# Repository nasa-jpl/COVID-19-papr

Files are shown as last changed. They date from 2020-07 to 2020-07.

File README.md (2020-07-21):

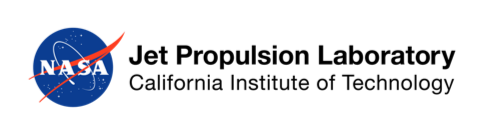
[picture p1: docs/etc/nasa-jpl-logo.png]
Jet Propulsion Laboratory, California Institute of Technology (NASA JPL)
 
# JPL Designed Powered Air-Purifying Respirator (PAPR)

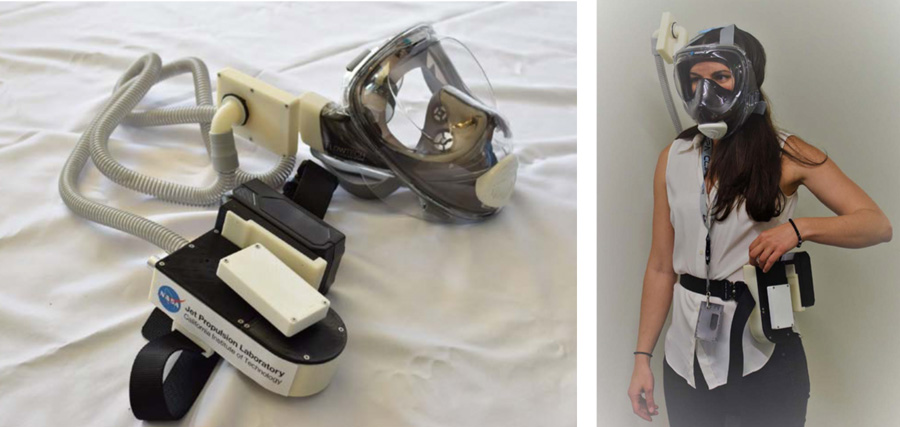
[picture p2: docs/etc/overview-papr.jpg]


In order to help provide Personal Protective Equipment (PPE) for the Coronavirus pandemic, a team at NASA’s Jet Propulsion Laboratory (JPL) has created and tested a 3D printable Powered Air-Purifying Respirator (PAPR) device with custom filters and Commercial Off-The-Shelf (COTS) components. Utilizing a Wildhorn Outfitters® Full Face Snorkel Mask and other COTS equipment, the JPL design is available for use by motivated creators in an Open Source forum readily accessible by anyone wishing to produce the device. Some testing has been performed by JPL and others to verify that it meets the design requirements identified in Public Health Title 42, Code of Federal Regulations, Part 84, but it lacks any NIOSH or other medical institution approval. The device is intended to provide a last line of defense when certified PAPRs are not commercially available.
 
## Getting Started

Read the [full documentation](docs/PAPR_Background_and_Instructions.pdf) to get started. Be sure to reference this document when reviewing the bill of materials and build files listed below.

➡️ [Full Documentation](docs/PAPR_Background_and_Instructions.pdf) 

## Materials Required

The JPL PAPR team has generated a [Bill of Materials (BOM)](docs/Bill_of_Materials.xlsx) for each of the two separate PAPR configurations. The PAPR System top assembly part number is 15180125 with the -1 version signifying the Globe Tools Blower version, and the -2 version signifying the ebmpapst Blower Motor version. These two different versions are functionally the same but slight design changes are included to manage the differences in the blower motor designs. The individual shopping lists are included as separate tabs in the BOM spreadsheet:

➡️ [Bill of Materials (BOM)](docs/Bill_of_Materials.xlsx)

## Build Files

Although the JPL PAPR design uses COTS parts, JPL designed 3D printed parts to package and support these COTS items so the system can perform the intended function. 3D printing enables the home user to download and fabricate these parts independently. The PAPR System top assembly part number is 15180125 with the -1 version signifying the Globe Tools Blower version, and the -2 version signifying the ebmpapst Blower Motor version. These two different versions are functionally the same but slight design changes are included to manage the differences in the blower motor designs.

➡️ [15180125-1 STL Files](15180125-1%20Globe%20Tools%20Blower) (Globe Tools Blower)  
➡️ [15180125-2 STL Files](15180125-2%20ebmPapst%20Blower) (ebmPapst Blower Motor)

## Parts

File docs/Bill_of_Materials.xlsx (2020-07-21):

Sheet: CURRENT BOM
 |  |  |  | PAPR Part and Materials List
 | QTY |  | ITEM NO | PART NO | PART NOMENCLATURE | MATERIAL OR NOTE | MANUFACTURER | Purchasing Link / CAD File Download Source | Minimum Materials Order |  | Price Per PAPR |  | Price Per PAPR |  | Comments
 |  |  |  |  |  |  |  |  |  |  | 105108125 - 1 |  | 105108125 - 2
 | -1 | -2 |  |  |  |  |  |  | Qty | Price, $ | Qty | Price, $ | Qty | Price, $
105108125 Powered Air Purifying Respirator Assembly | 1 | 1 | 1 | Seaview 180 V2 | Snorkel Mask |  | Wildhorn Outfitters | https://www.wildhornoutfitters.com/collections/snorkeling/products/seaview-180-v2-snorkel-mask?variant=10093212041252 | 1 | $74.99 | 1 | $74.99 | 1 | $74.99
 | 1 | 1 | 2 | P09 | Tactical Belt |  | Amazon / Fairwin | https://www.amazon.com/dp/B07V8RMB84/ref=pe_2640190_232748420_TE_item | 2 | $26.99 | 1 | $13.49 | 1 | $13.49 | 2 pack, only need 1. Any belt that can sustain the PAPR weight can be used.
 |  | 1 | 3 | 15180124-2 | Blower Assembly | ABS | JPL Assembly
 | 1 |  | 4 | 15180124-1 | Blower Assembly | ABS | JPL Assembly
 | 2 | 2 | 5 | 15180119-1 | Seal, Round, Filter Adapter | Multipurpose Neoprene Foam Strip | JPL Part |  |  |  |  |  |  |  | Make with 15180118-1, Template, Filter Seal, Round, 3D Printed
 | 1 | 1 | 6 | 15180122-1 | Filter Assembly | ABS | JPL Assembly
 | 1 | 1 | 7 | 15180109-1 | Hose Adapter | ABS | 3D Printed Component | JPL Github
 | 1 | 1 | 8 | 15180112-1 | SeaView 180 V2 Snorkel Mask Side Adapter | ABS | 3D Printed Component | JPL Github
 | QTY |  | ITEM NO | PART NO | PART NOMENCLATURE | MATERIAL OR NOTE | MANUFACTURER | Purchasing Link / CAD File Download Source | Minimum Materials Order |  | Price Per PAPR |  | Price Per PAPR |  | Comments
 |  |  |  |  |  |  |  |  |  |  | 105108125 - 1 |  | 105108125 - 2
 | -1 | -2 |  |  |  |  |  |  | Qty | Price, $ | Qty | Price, $ | Qty | Price, $
15180124 Blower Assembly | 1 | 1 | 9 | 5388k24 | Worm Clamp / Plumbers Tape |  | McMaster-Carr | https://www.mcmaster.com/catalog/5388K24 | 10 | $7.85 | 1 | $0.78 | 1 | $0.78 | OPTIONAL ITEM FOR -1 PAPR DESIGN, NECESSARY FOR -2 PAPR DESIGN 10 pack, need 1
 | 1 | 1 | 10 | SKU: 5797 | Hose, CPAP | Tubing Slim-Style, 48 Inch Length | CPAP SUPPLY USA | https://www.cpapsupplyusa.com/cpapsupplies/tubing/breascpaptubing4ftslim-style.html | 1 | $9.95 | 1 | $9.95 | 1 | $9.95
 | 21 | 23 | 11 | 90065A110 | Screw, C-Sink, Phillips | 18-8 CRES, #4-1/2 in long | McMaster-Carr | https://www.mcmaster.com/catalog/126/3152 | 100 | $3.50 | 21 | $0.73 | 23 | $0.81 | This item is repeated, do not purchase more than what is needed
 | 1 | 1 | 5 | 15180119-1 | Seal, Round, Filter Adapter | Multipurpose Neoprene Foam Strip | JPL Part |  |  |  |  |  |  |  | Make with 15180118-1, Template, Filter Seal, Round, 3D Printed
 | 1 | 1 | 12 | 2935202 | 24V 4ah Battery |  | greenworks | https://www.greenworkstools.com/24v-battery | 1 | $79.99 | 1 | $79.99 | 1 | $79.99 | The 24V, 2AH battery from greenworks will work too but battery life will be significantly reduced
 | 1 |  | 13 | SKU: 702554 | Tubing, 5/8 in ID x 3/4 in OD | Clear Vinyl | Home Depot | https://www.homedepot.com/p/UDP-5-8-in-I-D-x-3-4-in-O-D-x-10-ft-Clear-Vinyl-Tubing-T10006012/304185144 | 10 ft | $9.84 | 1 | $0.16 |  |  | You can replace this component ~ 60 times
 |  | 1 | 14 | 5233K47 | Tubing, 7/8 in ID, 1-1/8 in OD | Clear PVC Plastic | McMaster-Carr | https://www.mcmaster.com/#5233K47 | 10 ft | $14.90 |  |  | 1 | $0.25 | You can replace this component ~ 60 times
 | 1 | 1 | 15 | 15180123-1 | Inlet Filter Assembly |  | JPL Assembly
 | 1 | 1 | 16 | 15180121-1 | Low Flow Alarm System & Electronics Assembly |  | JPL Assembly
 |  | 1 | 17 | 15180101-2 | Housing, ebmpapst Blower |  | 3D Printed Component | JPL Github
 | 1 |  | 18 | 15180101-1 | Housing, Globe Tools Blower |  | 3D Printed Component | JPL Github
 | 1 | 1 | 19 | 15180102-1 | Blower Lid, Universal Blower |  | 3D Printed Component | JPL Github
 | 1 |  | 20 | 15180103-1 | Electronics Lid, Globe Tools Blower |  | 3D Printed Component | JPL Github
 |  | 1 | 21 | 15180103-2 | Electronics Lid, ebmpapst Blower |  | 3D Printed Component | JPL Github
 | 1 | 1 | 22 | 15180104-1 | Battery Holder, Universal Blower |  | 3D Printed Component | JPL Github
 | 2 | 2 | 23 | 15180105-1 | Belt Attachment, Universal Blower |  | 3D Printed Component | JPL Github
 |  | 1 | 24 | 15180107-1 | Blower Mount, ebmpapst Blower |  | 3D Printed Component | JPL Github
 |  | 1 | 25 | 15180108-1 | Controller Mount, ebmpapst Blower |  | 3D Printed Component | JPL Github
 | QTY |  | ITEM NO | PART NO | PART NOMENCLATURE | MATERIAL OR NOTE | MANUFACTURER | Purchasing Link / CAD File Download Source | Minimum Materials Order |  | Price Per PAPR |  | Price Per PAPR |  | Comments
 |  |  |  |  |  |  |  |  |  |  | 105108125 - 1 |  | 105108125 - 2
 | -1 |  |  |  |  |  |  |  | Qty | Price, $ | Qty | Price, $ | Qty | Price, $
15180123 Inlet Filter Assembly | 4 |  | 11 | 90065A110 | Screw, C-Sink, Phillips | 18-8 CRES, #4-1/2 in long | McMaster-Carr | https://www.mcmaster.com/catalog/126/3152 | 100 | $3.50 | 4 | $0.14 | 4 | $0.14 | This item is repeated, do not purchase more than what is needed
 | 1 |  | 26 | 53291 Style Q | HEPA Filter | HEPA Cloth Vacuum Bag | Kenmore | https://www.amazon.com/dp/B07DQ2ZXJV/ (https://www.amazon.com/dp/B07DQ2ZXJV/ref=pe_2640190_232748420_TE_item?th=1) | 2 | $19.99 | 2 | $4.00 | 2 | $4.00 | this is enough material to replace both filters ~ 5 times
 | 1 |  | 27 | 15180113-1 | Inlet Filter Base | ABS | 3D Printed Component | JPL Github
 | 1 |  | 28 | 15180114-1 | Inlet Filter Cover | ABS | 3D Printed Component | JPL Github
 | QTY |  | ITEM NO | PART NO | PART NOMENCLATURE | MATERIAL OR NOTE | MANUFACTURER | Purchasing Link / CAD File Download Source | Minimum Materials Order |  | Price Per PAPR |  | Price Per PAPR |  | Comments
 |  |  |  |  |  |  |  |  |  |  | 105108125 - 1 |  | 105108125 - 2
 | -1 |  |  |  |  |  |  |  | Qty | Price, $ | Qty | Price, $ | Qty | Price, $
15180122 Filter Assembly | 6 |  | 11 | 90065A110 | Screw, C-Sink, Phillips | 18-8 CRES, #4-1/2 in long | McMaster-Carr | https://www.mcmaster.com/catalog/126/3152 | 100 | $3.50 | 6 | $0.21 | 6 | $0.21 | This item is repeated, do not purchase more than what is needed
 | 1 |  | 29 | 93375K404 | Seal, Filter Material | Multipurpose Neoprene Foam Strip | McMaster-Carr | https://www.mcmaster.com/93375K404 | 1 | $14.00 | 1 | $3.50 | 1 | $3.50 | Make with 15180118-2, Template, Filter Seal, 3D Printed. This is enough material to replace seals ~ 4 times
 | 1 |  | 30 | 15180119-2 | Seal, Rectangular, Filter Adapter | Multipurpose Neoprene Foam Strip | JPL Part |  |  |  |  |  |  |  | Make with 15180118-2, Template, Filter Seal, 3D Printed
 | 1 |  | 26 | 53291 Style Q | HEPA Filter | HEPA Cloth Vacuum Bag | Kenmore | https://www.amazon.com/dp/B07DQ2ZXJV/ (https://www.amazon.com/dp/B07DQ2ZXJV/ref=pe_2640190_232748420_TE_item?th=1) | 2 | $19.99 | 2 | $4.00 | 2 | $4.00 | This item is repeated, do not purchase more than what is needed
 | 1 |  | 31 | 15180110-1 | Helmet Filter Base (Sealed 3m) | ABS | 3D Printed Component | JPL Github
 | 1 |  | 32 | 15180111-1 | Helmet Filter Cover (Sealed 3m) | ABS | 3D Printed Component | JPL Github
 | QTY |  | ITEM NO | PART NO | PART NOMENCLATURE | MATERIAL OR NOTE | MANUFACTURER | Purchasing Link / CAD File Download Source | Minimum Materials Order |  | Price Per PAPR |  | Price Per PAPR |  | Comments
 |  |  |  |  |  |  |  |  |  |  | 105108125 - 1 |  | 105108125 - 2
 | -1 |  |  |  |  |  |  |  | Qty | Price, $ | Qty | Price, $ | Qty | Price, $
15180121 Low Flow Sensor & Electronics | 4 |  | 33 | 96817A209 | Screw, Thread-Forming for Thin Plastic, Torx Hd | Zinc Plated Steel, M2 x 6mm long, | McMaster-Carr | https://www.mcmaster.com/catalog/126/3168 | 25 | $6.69 | 4 | $1.07 | 4 | $1.07 | This item is repeated, do not purchase more than what is needed
 | 1 |  | 34 | SFM3300-250-D | Flow Meter |  | Sensirion | https://www.digikey.com/product-detail/en/sensirion-ag/ | 1 | $41.80 | 1 | $41.80 | 1 | $41.80
 | 1 |  | 35 |  | Power Switch (2 state toggle switch) |  | Amazon | https://www.amazon.com/Gadgeter-125VAC-Position-Terminal | 20 | $11.00 | 1 | $0.55 | 1 | $0.55 | 20 pack, need 1
 | 1 |  | 36 | A000005 | Arduino Nano | (Controller for alarm system) | Arduino | https://store.arduino.cc/usa/arduino-nano | 1 | $20.70 | 1 | $20.70 | 1 | $20.70
 | 1 |  | 37 | MP1584EN | Voltage regulator | for Arduino | WGCD | https://www.amazon.com/MP1584EN-DC-DC-Converter-Adjustable-Module/ | 6 | $8.55 | 1 | $1.43 | 1 | $1.43 | Set to 5v and check with multimeter. Alternatively, use 5V set output version made by pololu. 6 pack, need 1
 | 1 |  | 38 | Red LED with Leads | LED | for alarm system | TT Electronics | https://www.digikey.com/product-detail/en/tt-electronics-optek-technology/ | 1 | $0.20 | 1 | $0.20 | 1 | $0.20 | Make sure to use resistor!
 | 1 |  | 39 | 220 Ohm Resistor | Resistor | for LED pull up | Stackpole Electronics | https://www.digikey.com/product-detail/en/stackpole-electronics-inc/ | 1 | $0.10 | 1 | $0.10 | 1 | $0.10 | Used for LED pull up
 | 1 |  | 40 | ECPB_SNAP_BK_3P | Prototype Board |  | ElectroCookie | https://www.amazon.com/gp/product/B08151V9TS/ref=ox_sc_act_title_6?smid=A1S21QI0S59A8I&psc=1 | 12 | $12.00 | 1 | $1.00 | 1 | $1.00 | 12 pack, need 1
 | 1 |  | 41 | a12081600ux0477 | Buzzer |  | Uxcell | https://www.amazon.com/gp/product/B00B0Q4KKO/ref=ox_sc_act_title_5?smid=ATVPDKIKX0DER&psc=1 | 5 | $6.00 | 1 | $1.20 | 1 | $1.20 | 5 pack, need 1
 | 1 |  | 42 |  | 1/8" x 4" Zip Ties |  |  |  |  |  |  |  | 0 | $0.00 | To secure voltage regulator
 | 1 |  | 43 | Jumper wire kit | Jumper wires for various electronics | 24 AWG | Austor | https://www.amazon.com/AUSTOR-Lengths-Assorted-Preformed-Breadboard/ | 1 | $10.99 | 1 | $10.99 | 1 | $10.99 | $10.99 for kit of various lengths. Any 24 AWG or larger wire should work.
 | QTY |  | ITEM NO | PART NO | PART NOMENCLATURE | MATERIAL OR NOTE | MANUFACTURER | Purchasing Link / CAD File Download Source | Minimum Materials Order |  | Price Per PAPR |  | Price Per PAPR |  | Comments
 |  |  |  |  |  |  |  |  |  |  | 105108125 - 1 |  | 105108125 - 2
 | -1 | -2 |  |  |  |  |  |  | Qty | Price, $ | Qty | Price, $ | Qty | Price, $
15180120 Blower Base Electronics | 4 |  | 33 | 96817A209 | Screw, Thread-Forming for Thin Plastic, Torx Hd | Zinc Plated Steel, M2 x 6mm long, | McMaster-Carr | https://www.mcmaster.com/catalog/126/3168 | 25 | $6.69 | 4 | $1.07 |  |  | This item is repeated, do not purchase more than what is needed
 | 1 | 1 | 44 | 8110K1 | Inline Fuse Holder |  | McMaster-Carr | https://www.mcmaster.com/8110K1-8110K1 | 1 | $3.18 | 1 | $3.18 | 1 | $3.18 | Can get these at an auto parts store
 | 1 | 1 | 45 | 7460K521 | Fuse, 2 Amp | ATM mini blade | McMaster-Carr | https://www.mcmaster.com/7460K521 | 5 | $2.61 | 1 | $0.52 | 1 | $0.52 | Can get these at an auto parts store
 | 2 | 2 | 46 | 7060K88 | Single Crimp Male Quick Disconnect Terminal |  | McMaster-Carr | https://www.mcmaster.com/7060K88-7060K88 | 10 | $3.43 | 2 | $0.69 | 2 | $0.69 | 10 pack, need 2
 |  | 1 | 47 | VA-RV45-PAPR | Control Potentiometer |  | ebmpapst | https://www.masterelectronics.com/news/170-free-open-source-respirator-design-from-nasa.aspx | 1 | $0.00 |  |  | 1 | $0.00 | Blower, controller and potentiometer sold in a kit
 |  | 1 | 48 |  | Brushless DC Blower Control Board
 |  | 1 | 49 |  | Brushless DC Blower
 | 1 |  | 50 | WM7040-24V | Control Potentiometer |  | greenworks / Globe Tool |  | 1 | $0.00 | 1 | $0.00 |  |  | Blower, controller and potentiometer sold in a kit
 | 1 |  | 51 |  | Brushless DC Blower Control Board
 | 1 |  | 52 |  | Brushless DC Blower | Manufacturer did continuous operations test 4 hours
 | 1 | 1 | 53 | 16 Gauge Silicone wire | 16 Gauge Silicone wire | 18" of 16 AWG Wire | BNTECHGO | https://smile.amazon.com/BNTECHGO-Silicone-Flexible-Strands-Stranded/dp/B017TFR664 | 1 | $8.48 | 1 | $1.27 | 1 | $1.27 | For use with crimped quick disconnects for battery power. Any 16 AWG or 14 AWG wire should work.
 |  |  |  |  |  |  |  |  | Minimum Materials Order |  | Minimum Supplies Needed
 |  |  |  |  |  |  |  |  | Price, $ |  | Price, $
 |  |  |  | PAPR, 105108125 - 1 |  |  |  |  | $374.98 |  | $276.94
 |  |  |  | PAPR, 105108125 - 2 |  |  |  |  | $387.89 |  | $276.80

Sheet: Shopping List -1 (Globe Tools)
 |  |  | PAPR Part and Materials List
 | QTY | ITEM NO | PART NO | PART NOMENCLATURE | MATERIAL OR NOTE | MANUFACTURER | Purchasing Link / CAD File Download Source | Minimum Materials Order |  | Price Per PAPR |  | Price Per PAPR |  | Comments
 |  |  |  |  |  |  |  |  |  | 105108125 - 1 |  | 105108125 - 2
 |  |  |  |  |  |  |  | Qty | Price, $ | Qty | Price, $ | Qty | Price, $
105108125 Powered Air Purifying Respirator Assembly | 1 | 1 | Seaview 180 V2 | Snorkel Mask | 0 | Wildhorn Outfitters | https://www.wildhornoutfitters.com/collections/snorkeling/products/seaview-180-v2-snorkel-mask?variant=10093212041252 | 1 | $74.99 | 1 | $74.99 | 1 | $74.99 | 0
 | 1 | 2 | P09 | Tactical Belt | 0 | Amazon / Fairwin | https://www.amazon.com/dp/B07V8RMB84/ref=pe_2640190_232748420_TE_item | 2 | $26.99 | 1 | $13.49 | 1 | $13.49 | 2 pack, only need 1. Any belt that can sustain the PAPR weight can be used.
15180124 Blower Assembly | 1 | 9 | 5388k24 | Worm Clamp / Plumbers Tape | 0 | McMaster-Carr | https://www.mcmaster.com/catalog/5388K24 | 10 | $7.85 | 1 | $0.78 | 1 | $0.78 | OPTIONAL ITEM FOR -1 PAPR DESIGN, NECESSARY FOR -2 PAPR DESIGN 10 pack, need 1
 | 1 | 10 | SKU: 5797 | Hose, CPAP | Tubing Slim-Style, 48 Inch Length | CPAP SUPPLY USA | https://www.cpapsupplyusa.com/cpapsupplies/tubing/breascpaptubing4ftslim-style.html | 1 | $9.95 | 1 | $9.95 | 1 | $9.95 | 0
 | 21 | 11 | 90065A110 | Screw, C-Sink, Phillips | 18-8 CRES, #4-1/2 in long | McMaster-Carr | https://www.mcmaster.com/catalog/126/3152 | 100 | $3.50 | 21 | $0.73 | 23 | $0.81 | This item is repeated, do not purchase more than what is needed
 | 1 | 12 | 2935202 | 24V 4ah Battery | 0 | greenworks | https://www.greenworkstools.com/24v-battery | 1 | $79.99 | 1 | $79.99 | 1 | $79.99 | The 24V, 2AH battery from greenworks will work too but battery life will be significantly reduced
 | 1 | 13 | SKU: 702554 | Tubing, 5/8 in ID x 3/4 in OD | Clear Vinyl | Home Depot | https://www.homedepot.com/p/UDP-5-8-in-I-D-x-3-4-in-O-D-x-10-ft-Clear-Vinyl-Tubing-T10006012/304185144 | 10 ft | $9.84 | 1 | $0.16 | 0 |  | You can replace this component ~ 60 times
15180123 Inlet Filter Assembly | 4 | 11 | 90065A110 | Screw, C-Sink, Phillips | 18-8 CRES, #4-1/2 in long | McMaster-Carr | https://www.mcmaster.com/catalog/126/3152 | 100 | $3.50 | 4 | $0.14 | 4 | $0.14 | This item is repeated, do not purchase more than what is needed
 | 1 | 26 | 53291 Style Q | HEPA Filter | HEPA Cloth Vacuum Bag | Kenmore | https://www.amazon.com/dp/B07DQ2ZXJV/ | 2 | $19.99 | 2 | $4.00 | 2 | $4.00 | this is enough material to replace both filters ~ 5 times
15180122 Filter Assembly | 6 | 11 | 90065A110 | Screw, C-Sink, Phillips | 18-8 CRES, #4-1/2 in long | McMaster-Carr | https://www.mcmaster.com/catalog/126/3152 | 100 | $3.50 | 6 | $0.21 | 6 | $0.21 | This item is repeated, do not purchase more than what is needed
 | 1 | 29 | 93375K404 | Seal, Filter Material | Multipurpose Neoprene Foam Strip | McMaster-Carr | https://www.mcmaster.com/93375K404 | 1 | $14.00 | 1 | $3.50 | 1 | $3.50 | Make with 15180118-2, Template, Filter Seal, 3D Printed. This is enough material to replace seals ~ 4 times
 | 1 | 26 | 53291 Style Q | HEPA Filter | HEPA Cloth Vacuum Bag | Kenmore | https://www.amazon.com/dp/B07DQ2ZXJV/ | 2 | $19.99 | 2 | $4.00 | 2 | $4.00 | This item is repeated, do not purchase more than what is needed
15180121 Low Flow Sensor & Electronics | 4 | 33 | 96817A209 | Screw, Thread-Forming for Thin Plastic, Torx Hd | Zinc Plated Steel, M2 x 6mm long, | McMaster-Carr | https://www.mcmaster.com/catalog/126/3168 | 25 | $6.69 | 4 | $1.07 | 4 | $1.07 | This item is repeated, do not purchase more than what is needed
 | 1 | 34 | SFM3300-250-D | Flow Meter | 0 | Sensirion | https://www.digikey.com/product-detail/en/sensirion-ag/ | 1 | $41.80 | 1 | $41.80 | 1 | $41.80 | 0
 | 1 | 35 | 0 | Power Switch (2 state toggle switch) | 0 | Amazon | https://www.amazon.com/Gadgeter-125VAC-Position-Terminal | 20 | $11.00 | 1 | $0.55 | 1 | $0.55 | 20 pack, need 1
 | 1 | 36 | A000005 | Arduino Nano | (Controller for alarm system) | Arduino | https://store.arduino.cc/usa/arduino-nano | 1 | $20.70 | 1 | $20.70 | 1 | $20.70 | 0
 | 1 | 37 | MP1584EN | Voltage regulator | for Arduino | WGCD | https://www.amazon.com/MP1584EN-DC-DC-Converter-Adjustable-Module/ | 6 | $8.55 | 1 | $1.43 | 1 | $1.43 | Set to 5v and check with multimeter. Alternatively, use 5V set output version made by pololu. 6 pack, need 1
 | 1 | 38 | Red LED with Leads | LED | for alarm system | TT Electronics | https://www.digikey.com/product-detail/en/tt-electronics-optek-technology/ | 1 | $0.20 | 1 | $0.20 | 1 | $0.20 | Make sure to use resistor!
 | 1 | 39 | 220 Ohm Resistor | Resistor | for LED pull up | Stackpole Electronics | https://www.digikey.com/product-detail/en/stackpole-electronics-inc/ | 1 | $0.10 | 1 | $0.10 | 1 | $0.10 | Used for LED pull up
 | 1 | 40 | ECPB_SNAP_BK_3P | Prototype Board | 0 | ElectroCookie | https://www.amazon.com/gp/product/B08151V9TS/ref=ox_sc_act_title_6?smid=A1S21QI0S59A8I&psc=1 | 12 | $12.00 | 1 | $1.00 | 1 | $1.00 | 12 pack, need 1
 | 1 | 41 | a12081600ux0477 | Buzzer | 0 | Uxcell | https://www.amazon.com/gp/product/B00B0Q4KKO/ref=ox_sc_act_title_5?smid=ATVPDKIKX0DER&psc=1 | 5 | $6.00 | 1 | $1.20 | 1 | $1.20 | 5 pack, need 1
 | 1 | 42 | 0 | 1/8" x 4" Zip Ties | 0 | 0 | 0 | 0 | $0.00 | 0 | $0.00 | 0 | $0.00 | To secure voltage regulator
 | 1 | 43 | Jumper wire kit | Jumper wires for various electronics | 24 AWG | Austor | https://www.amazon.com/AUSTOR-Lengths-Assorted-Preformed-Breadboard/ | 1 | $10.99 | 1 | $10.99 | 1 | $10.99 | $10.99 for kit of various lengths. Any 24 AWG or larger wire should work.
15180120 Blower Base Electronics | 4 | 33 | 96817A209 | Screw, Thread-Forming for Thin Plastic, Torx Hd | Zinc Plated Steel, M2 x 6mm long, | McMaster-Carr | https://www.mcmaster.com/catalog/126/3168 | 25 | $6.69 | 4 | $1.07 | 0 |  | This item is repeated, do not purchase more than what is needed
 | 1 | 44 | 8110K1 | Inline Fuse Holder | 0 | McMaster-Carr | https://www.mcmaster.com/8110K1-8110K1 | 1 | $3.18 | 1 | $3.18 | 1 | $3.18 | Can get these at an auto parts store
 | 1 | 45 | 7460K521 | Fuse, 2 Amp | ATM mini blade | McMaster-Carr | https://www.mcmaster.com/7460K521 | 5 | $2.61 | 1 | $0.52 | 1 | $0.52 | Can get these at an auto parts store
 | 2 | 46 | 7060K88 | Single Crimp Male Quick Disconnect Terminal | 0 | McMaster-Carr | https://www.mcmaster.com/7060K88-7060K88 | 10 | $3.43 | 2 | $0.69 | 2 | $0.69 | 10 pack, need 2
 | 1 | 50 | WM7040-24V | Control Potentiometer | 0 | greenworks / Globe Tool | 0 | 1 | $0.00 | 1 | $0.00 | 0 |  | Blower, controller and potentiometer sold in a kit
 | 1 | 51 |  | Brushless DC Blower Control Board | 0
 | 1 | 52 |  | Brushless DC Blower | Manufacturer did continuous operations test 4 hours
 | 1 | 53 | 16 Gauge Silicone wire | 16 Gauge Silicone wire | 18" of 16 AWG Wire | BNTECHGO | https://smile.amazon.com/BNTECHGO-Silicone-Flexible-Strands-Stranded/dp/B017TFR664 | 1 | $8.48 | 1 | $1.27 | 1 | $1.27 | For use with crimped quick disconnects for battery power. Any 16 AWG or 14 AWG wire should work.
 |  |  |  |  |  |  |  | Minimum Materials Order |  | Minimum Supplies Needed
 |  |  |  |  |  |  |  | Price, $ |  | Price, $
 |  |  | PAPR, 105108125 - 2 |  |  |  |  | $387.89 |  | $276.80

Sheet: Shopping List -2 (ebmPapst)
 |  |  | PAPR Part and Materials List |  |  |  |  |  |  |  |  |  |  | 0
 |  |  |  |  |  |  |  |  |  |  |  |  |  | 0
 | QTY | ITEM NO | PART NO | PART NOMENCLATURE | MATERIAL OR NOTE | MANUFACTURER | Purchasing Link / CAD File Download Source | Minimum Materials Order |  | Price Per PAPR |  | Price Per PAPR |  | Comments
 |  |  |  |  |  |  |  |  |  | 105108125 - 1 |  | 105108125 - 2
 |  |  |  |  |  |  |  | Qty | Price, $ | Qty | Price, $ | Qty | Price, $
105108125 Powered Air Purifying Respirator Assembly | 1 | 1 | Seaview 180 V2 | Snorkel Mask | 0 | Wildhorn Outfitters | https://www.wildhornoutfitters.com/collections/snorkeling/products/seaview-180-v2-snorkel-mask?variant=10093212041252 | 1 | $74.99 | 1 | $74.99 | 1 | $74.99 | 0
 | 1 | 2 | P09 | Tactical Belt | 0 | Amazon / Fairwin | https://www.amazon.com/dp/B07V8RMB84/ref=pe_2640190_232748420_TE_item | 2 | $26.99 | 1 | $13.49 | 1 | $13.49 | 2 pack, only need 1. Any belt that can sustain the PAPR weight can be used.
15180124 Blower Assembly | 1 | 9 | 5388k24 | Worm Clamp / Plumbers Tape | 0 | McMaster-Carr | https://www.mcmaster.com/catalog/5388K24 | 10 | $7.85 | 1 | $0.78 | 1 | $0.78 | OPTIONAL ITEM FOR -1 PAPR DESIGN, NECESSARY FOR -2 PAPR DESIGN 10 pack, need 1
 | 1 | 10 | SKU: 5797 | Hose, CPAP | Tubing Slim-Style, 48 Inch Length | CPAP SUPPLY USA | https://www.cpapsupplyusa.com/cpapsupplies/tubing/breascpaptubing4ftslim-style.html | 1 | $9.95 | 1 | $9.95 | 1 | $9.95 | 0
 | 23 | 11 | 90065A110 | Screw, C-Sink, Phillips | 18-8 CRES, #4-1/2 in long | McMaster-Carr | https://www.mcmaster.com/catalog/126/3152 | 100 | $3.50 | 21 | $0.73 | 23 | $0.81 | This item is repeated, do not purchase more than what is needed
 | 1 | 12 | 2935202 | 24V 4ah Battery | 0 | greenworks | https://www.greenworkstools.com/24v-battery | 1 | $79.99 | 1 | $79.99 | 1 | $79.99 | The 24V, 2AH battery from greenworks will work too but battery life will be significantly reduced
 | 1 | 14 | 5233K47 | Tubing, 7/8 in ID, 1-1/8 in OD | Clear PVC Plastic | McMaster-Carr | https://www.mcmaster.com/#5233K47 | 10 ft | $14.90 | 0 |  | 1 | $0.25 | You can replace this component ~ 60 times
15180123 Inlet Filter Assembly | 0 | 11 | 90065A110 | Screw, C-Sink, Phillips | 18-8 CRES, #4-1/2 in long | McMaster-Carr | https://www.mcmaster.com/catalog/126/3152 | 100 | $3.50 | 4 | $0.14 | 4 | $0.14 | This item is repeated, do not purchase more than what is needed
 | 0 | 26 | 53291 Style Q | HEPA Filter | HEPA Cloth Vacuum Bag | Kenmore | https://www.amazon.com/dp/B07DQ2ZXJV/ | 2 | $19.99 | 2 | $4.00 | 2 | $4.00 | this is enough material to replace both filters ~ 5 times
15180122 Filter Assembly | 0 | 11 | 90065A110 | Screw, C-Sink, Phillips | 18-8 CRES, #4-1/2 in long | McMaster-Carr | https://www.mcmaster.com/catalog/126/3152 | 100 | $3.50 | 6 | $0.21 | 6 | $0.21 | This item is repeated, do not purchase more than what is needed
 | 0 | 29 | 93375K404 | Seal, Filter Material | Multipurpose Neoprene Foam Strip | McMaster-Carr | https://www.mcmaster.com/93375K404 | 1 | $14.00 | 1 | $3.50 | 1 | $3.50 | Make with 15180118-2, Template, Filter Seal, 3D Printed. This is enough material to replace seals ~ 4 times
 | 0 | 26 | 53291 Style Q | HEPA Filter | HEPA Cloth Vacuum Bag | Kenmore | https://www.amazon.com/dp/B07DQ2ZXJV/ | 2 | $19.99 | 2 | $4.00 | 2 | $4.00 | This item is repeated, do not purchase more than what is needed
15180121 Low Flow Sensor & Electronics | 0 | 33 | 96817A209 | Screw, Thread-Forming for Thin Plastic, Torx Hd | Zinc Plated Steel, M2 x 6mm long, | McMaster-Carr | https://www.mcmaster.com/catalog/126/3168 | 25 | $6.69 | 4 | $1.07 | 4 | $1.07 | This item is repeated, do not purchase more than what is needed
 | 0 | 34 | SFM3300-250-D | Flow Meter | 0 | Sensirion | https://www.digikey.com/product-detail/en/sensirion-ag/ | 1 | $41.80 | 1 | $41.80 | 1 | $41.80 | 0
 | 0 | 35 | 0 | Power Switch (2 state toggle switch) | 0 | Amazon | https://www.amazon.com/Gadgeter-125VAC-Position-Terminal | 20 | $11.00 | 1 | $0.55 | 1 | $0.55 | 20 pack, need 1
 | 0 | 36 | A000005 | Arduino Nano | (Controller for alarm system) | Arduino | https://store.arduino.cc/usa/arduino-nano | 1 | $20.70 | 1 | $20.70 | 1 | $20.70 | 0
 | 0 | 37 | MP1584EN | Voltage regulator | for Arduino | WGCD | https://www.amazon.com/MP1584EN-DC-DC-Converter-Adjustable-Module/ | 6 | $8.55 | 1 | $1.43 | 1 | $1.43 | Set to 5v and check with multimeter. Alternatively, use 5V set output version made by pololu. 6 pack, need 1
 | 0 | 38 | Red LED with Leads | LED | for alarm system | TT Electronics | https://www.digikey.com/product-detail/en/tt-electronics-optek-technology/ | 1 | $0.20 | 1 | $0.20 | 1 | $0.20 | Make sure to use resistor!
 | 0 | 39 | 220 Ohm Resistor | Resistor | for LED pull up | Stackpole Electronics | https://www.digikey.com/product-detail/en/stackpole-electronics-inc/ | 1 | $0.10 | 1 | $0.10 | 1 | $0.10 | Used for LED pull up
 | 0 | 40 | ECPB_SNAP_BK_3P | Prototype Board | 0 | ElectroCookie | https://www.amazon.com/gp/product/B08151V9TS/ref=ox_sc_act_title_6?smid=A1S21QI0S59A8I&psc=1 | 12 | $12.00 | 1 | $1.00 | 1 | $1.00 | 12 pack, need 1
 | 0 | 41 | a12081600ux0477 | Buzzer | 0 | Uxcell | https://www.amazon.com/gp/product/B00B0Q4KKO/ref=ox_sc_act_title_5?smid=ATVPDKIKX0DER&psc=1 | 5 | $6.00 | 1 | $1.20 | 1 | $1.20 | 5 pack, need 1
 | 0 | 42 | 0 | 1/8" x 4" Zip Ties | 0 | 0 | 0 | 0 | $0.00 | 0 | $0.00 | 0 | $0.00 | To secure voltage regulator
 | 0 | 43 | Jumper wire kit | Jumper wires for various electronics | 24 AWG | Austor | https://www.amazon.com/AUSTOR-Lengths-Assorted-Preformed-Breadboard/ | 1 | $10.99 | 1 | $10.99 | 1 | $10.99 | $10.99 for kit of various lengths. Any 24 AWG or larger wire should work.
15180120 Blower Base Electronics | 1 | 44 | 8110K1 | Inline Fuse Holder | 0 | McMaster-Carr | https://www.mcmaster.com/8110K1-8110K1 | 1 | $3.18 | 1 | $3.18 | 1 | $3.18 | Can get these at an auto parts store
 | 1 | 45 | 7460K521 | Fuse, 2 Amp | ATM mini blade | McMaster-Carr | https://www.mcmaster.com/7460K521 | 5 | $2.61 | 1 | $0.52 | 1 | $0.52 | Can get these at an auto parts store
 | 2 | 46 | 7060K88 | Single Crimp Male Quick Disconnect Terminal | 0 | McMaster-Carr | https://www.mcmaster.com/7060K88-7060K88 | 10 | $3.43 | 2 | $0.69 | 2 | $0.69 | 10 pack, need 2
 | 1 | 47 | VA-RV45-PAPR | Control Potentiometer | 0 | ebmpapst | https://www.masterelectronics.com/news/170-free-open-source-respirator-design-from-nasa.aspx | 1 | $0.00 | 0 |  | 1 | $0.00 | Blower, controller and potentiometer sold in a kit
 | 1 | 48 |  | Brushless DC Blower Control Board | 0
 | 1 | 49 |  | Brushless DC Blower | 0
 | 1 | 53 | 16 Gauge Silicone wire | 16 Gauge Silicone wire | 18" of 16 AWG Wire | BNTECHGO | https://smile.amazon.com/BNTECHGO-Silicone-Flexible-Strands-Stranded/dp/B017TFR664 | 1 | $8.48 | 1 | $1.27 | 1 | $1.27 | For use with crimped quick disconnects for battery power. Any 16 AWG or 14 AWG wire should work.
 |  |  |  |  |  |  |  | Minimum Materials Order |  | Minimum Supplies Needed
 |  |  |  |  |  |  |  | Price, $ |  | Price, $
 |  |  | PAPR, 105108125 - 2 |  |  |  |  | $387.89 |  | $276.80

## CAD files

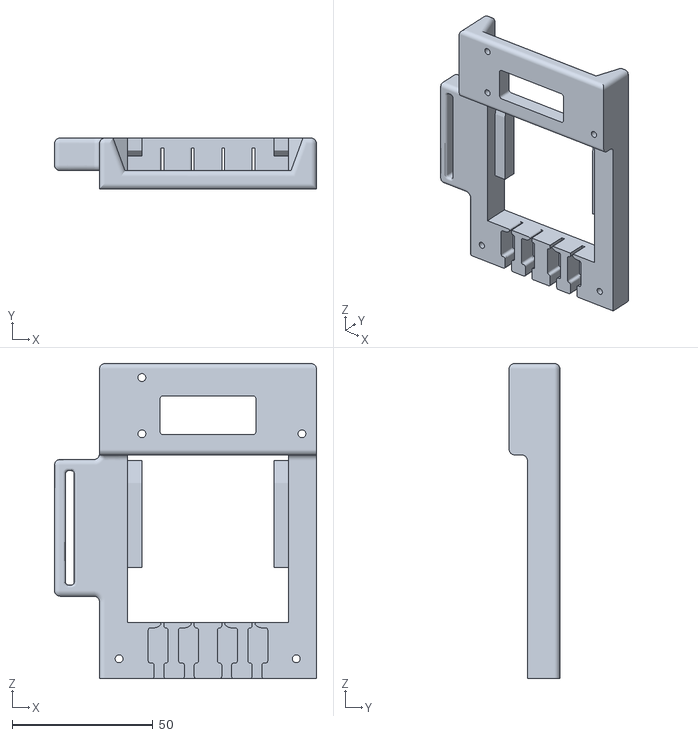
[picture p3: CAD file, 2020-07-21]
15180125-1 Globe Tools Blower/15180104-1_STL.STL
93.2 x 18.1 x 112.0

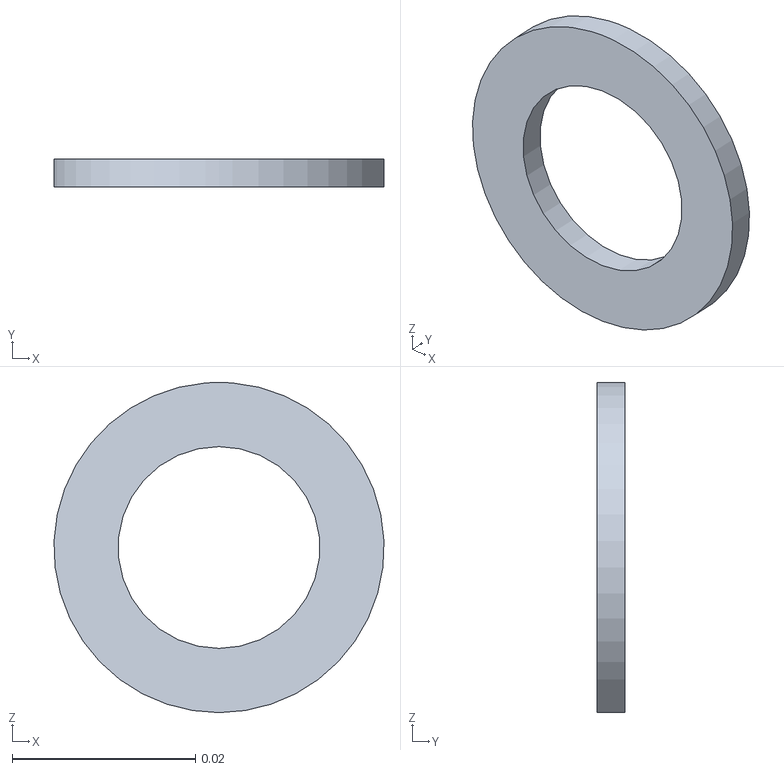
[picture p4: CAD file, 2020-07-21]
15180125-2 ebmPapst Blower/15180118-1_STL.STL
0.036 x 0.003 x 0.036

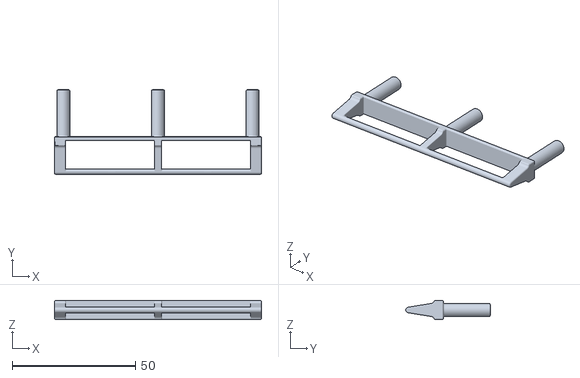
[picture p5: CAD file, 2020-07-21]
15180125-1 Globe Tools Blower/15180116-1_STL.STL
84.0 x 34.3 x 7.75

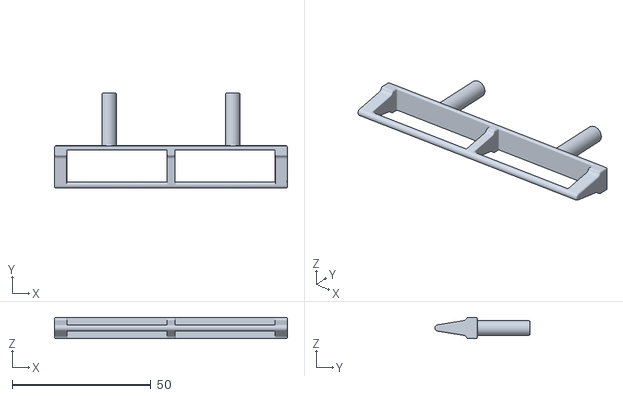
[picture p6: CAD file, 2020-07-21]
15180125-2 ebmPapst Blower/15180117-1_STL.STL
84.0 x 34.3 x 7.75

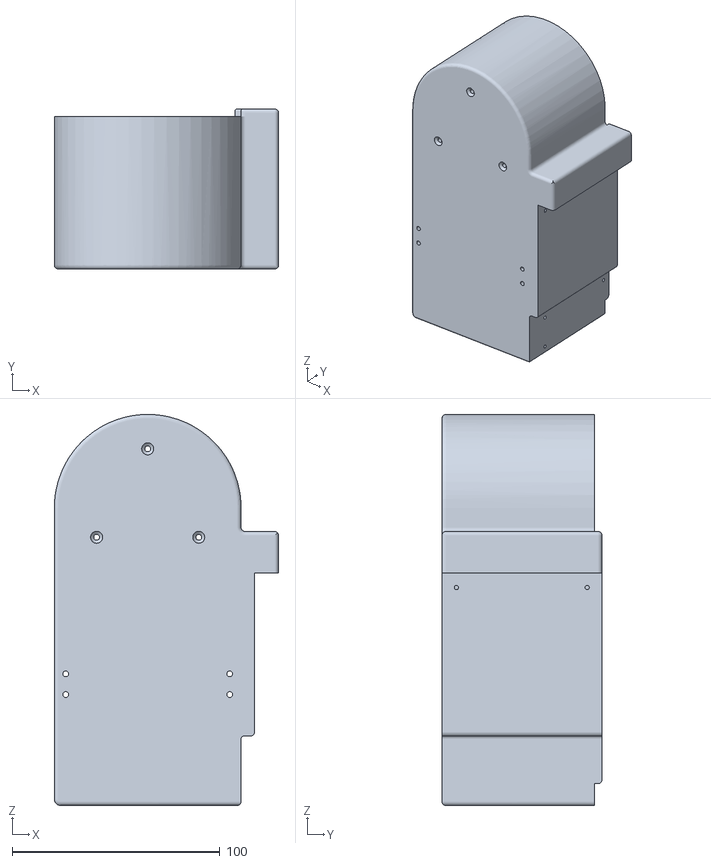
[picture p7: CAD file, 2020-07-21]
15180125-1 Globe Tools Blower/15180101-1_STL.STL
108.1 x 77.2 x 188.4

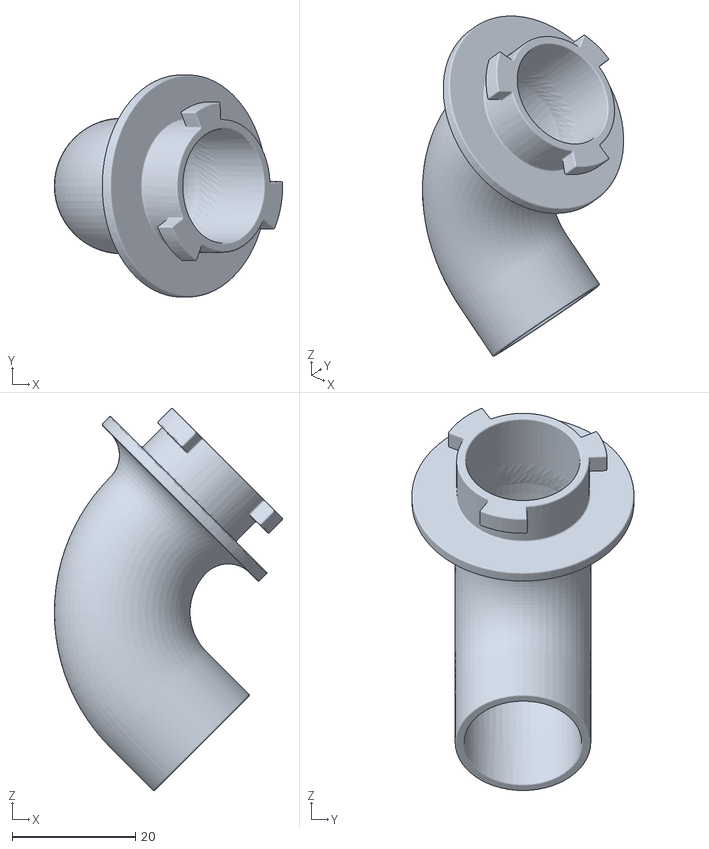
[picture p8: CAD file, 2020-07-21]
15180125-2 ebmPapst Blower/15180109-1_STL.STL
37.0 x 36.0 x 61.9

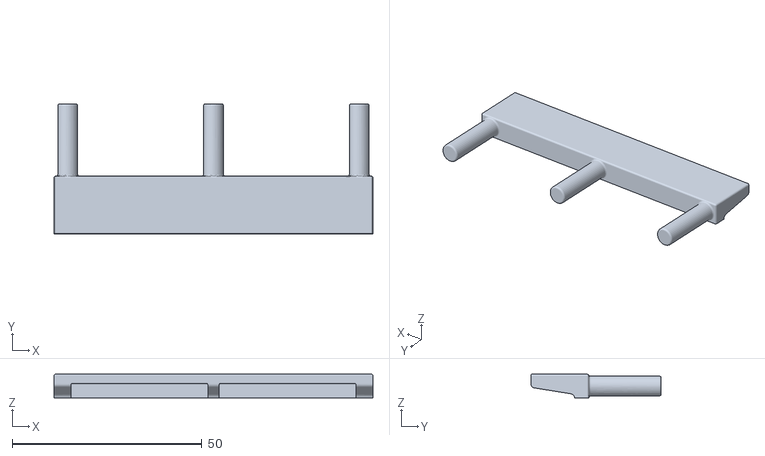
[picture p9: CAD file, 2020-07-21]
15180125-1 Globe Tools Blower/15180115-1_STL.STL
84.0 x 34.3 x 6.25

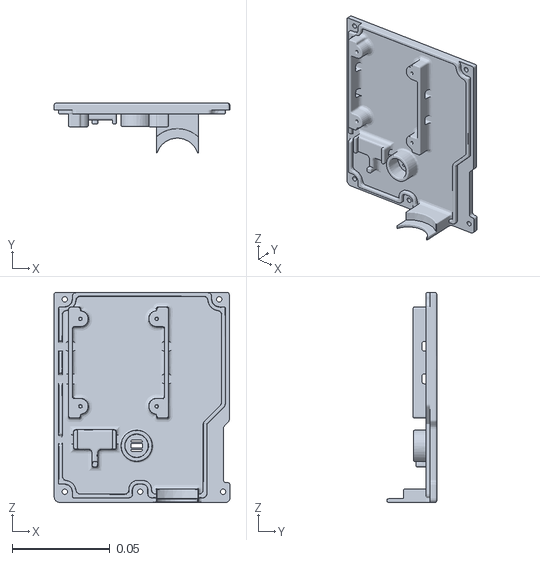
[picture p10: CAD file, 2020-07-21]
15180125-2 ebmPapst Blower/15180103-2_STL.STL
0.09 x 0.0254 x 0.107

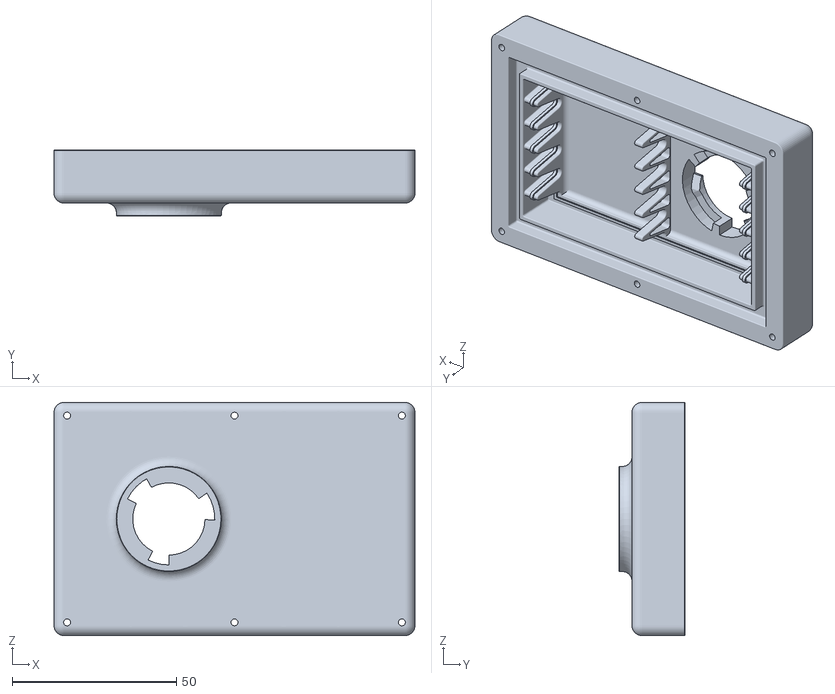
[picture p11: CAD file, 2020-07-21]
15180125-1 Globe Tools Blower/15180110-1_STL.STL
110.0 x 20.2 x 71.0

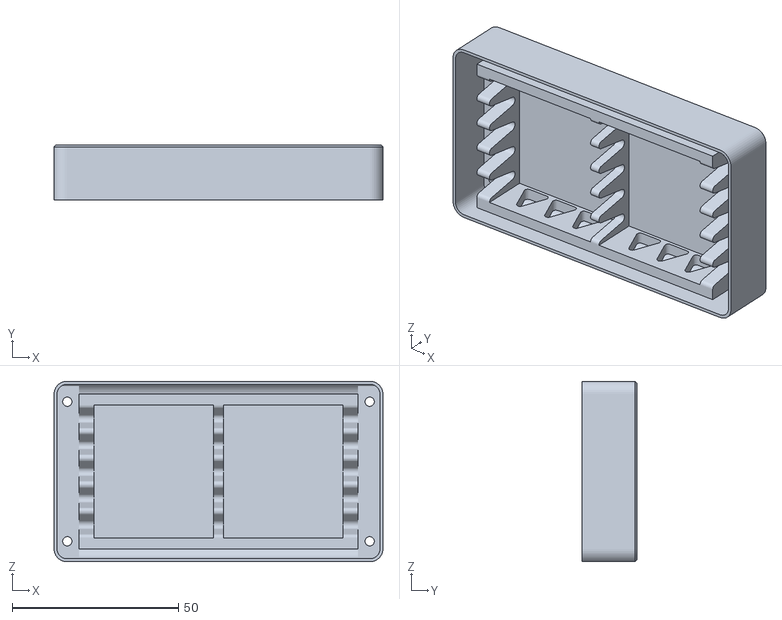
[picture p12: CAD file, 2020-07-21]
15180125-2 ebmPapst Blower/15180114-1_STL.STL
99.0 x 16.6 x 54.3

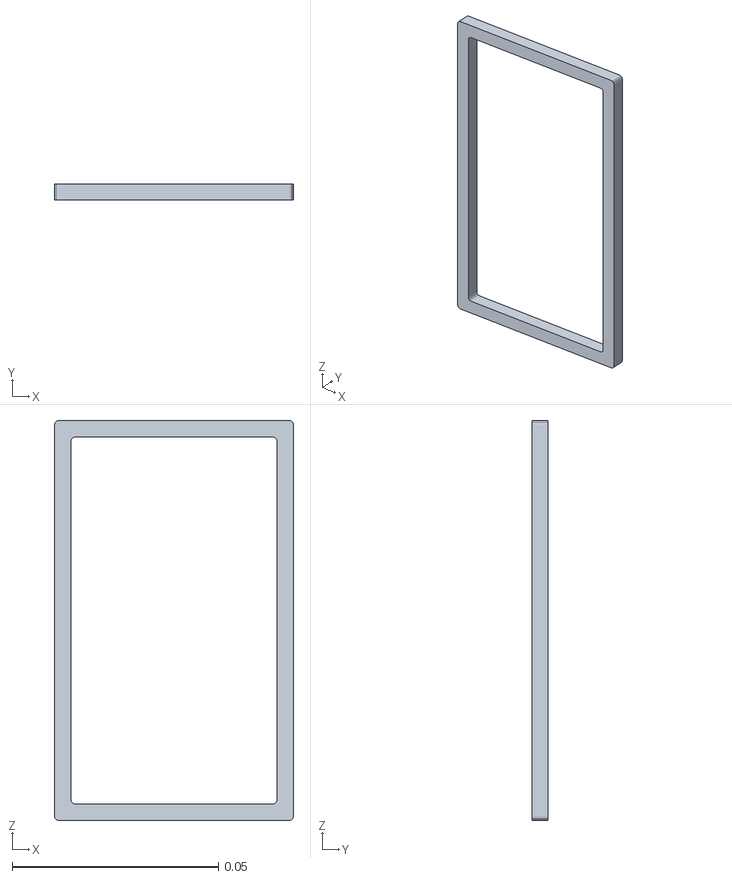
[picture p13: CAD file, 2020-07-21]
15180125-1 Globe Tools Blower/15180118-2_STL.STL
0.058 x 0.004 x 0.097

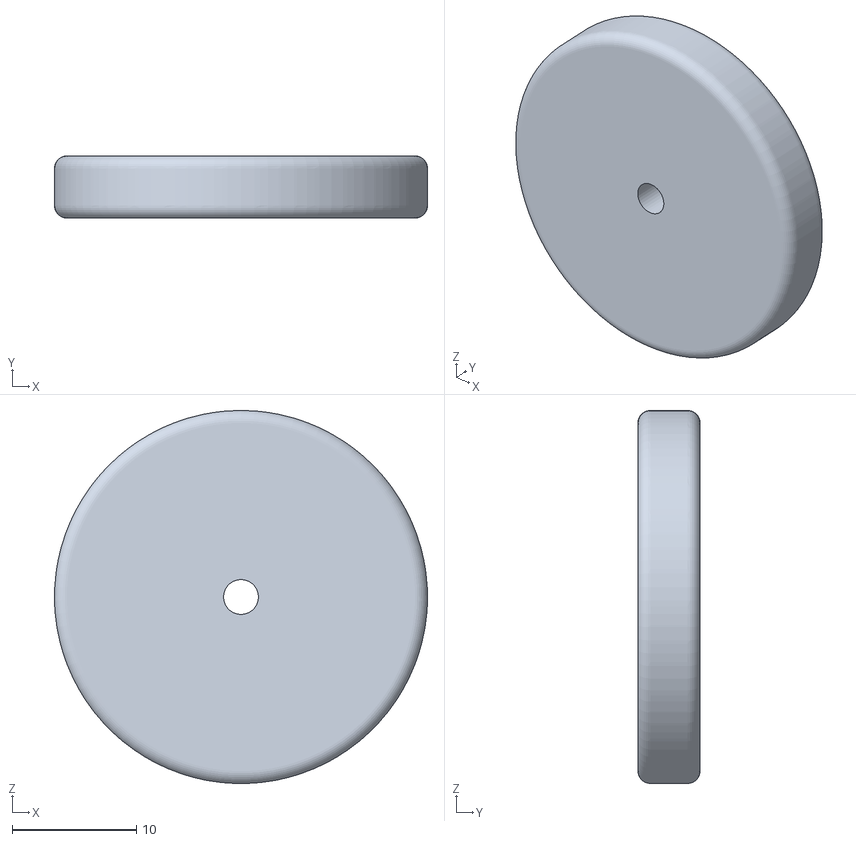
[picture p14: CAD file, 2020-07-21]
15180125-2 ebmPapst Blower/15180108-1_STL.STL
30.0 x 5.00 x 30.0

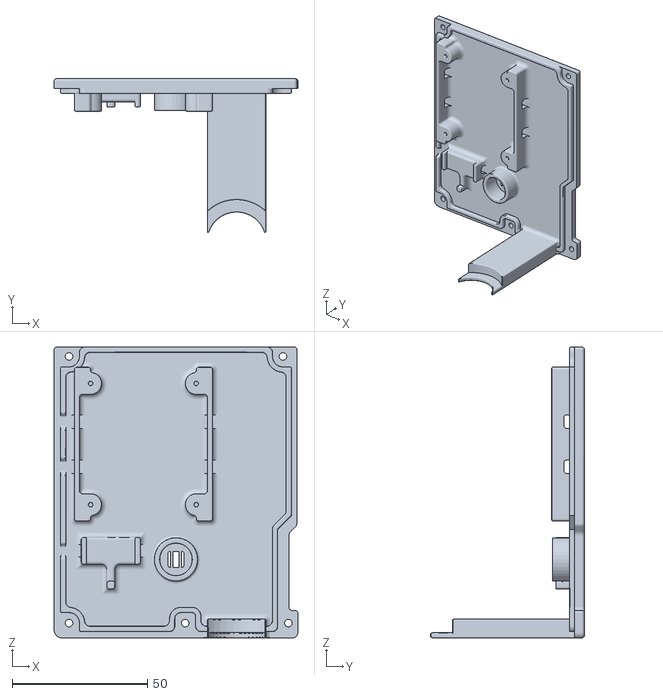
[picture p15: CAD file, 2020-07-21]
15180125-1 Globe Tools Blower/15180103-1_STL.STL
90.0 x 56.8 x 107.4

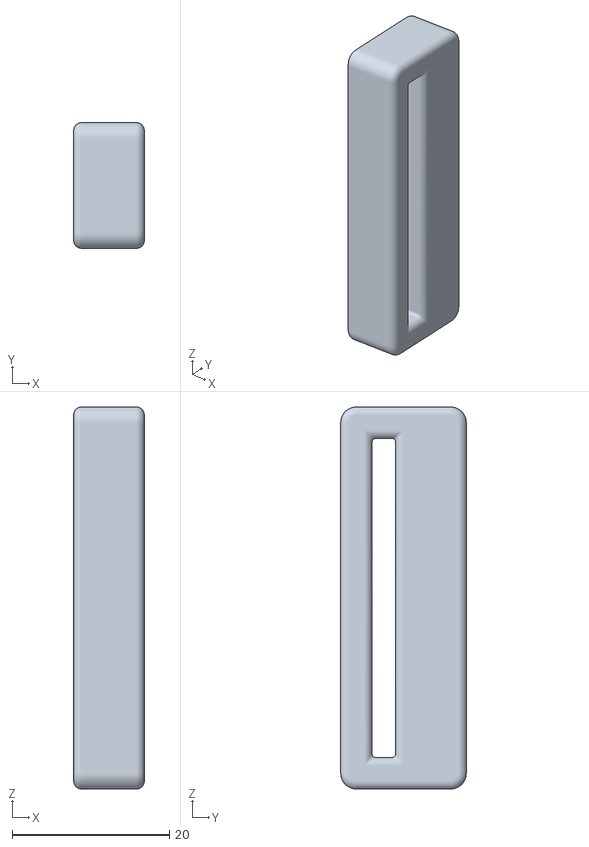
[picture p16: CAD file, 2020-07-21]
15180125-2 ebmPapst Blower/15180105-1_STL.STL
9.00 x 16.0 x 48.6

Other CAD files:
15180125-1 Globe Tools Blower/15180113-1_STL.STL
15180125-2 ebmPapst Blower/15180107-1_STL.STL
15180125-1 Globe Tools Blower/15180102-1_STL.STL
15180125-1 Globe Tools Blower/15180111-1_STL.STL
15180125-1 Globe Tools Blower/15180112-1_STL.STL
15180125-2 ebmPapst Blower/15180101-2_STL.STL
15180125-2 ebmPapst Blower/15180102-1_STL.STL
15180125-2 ebmPapst Blower/15180111-1_STL.STL
15180125-2 ebmPapst Blower/15180112-1_STL.STL
15180125-2 ebmPapst Blower/15180113-1_STL.STL
